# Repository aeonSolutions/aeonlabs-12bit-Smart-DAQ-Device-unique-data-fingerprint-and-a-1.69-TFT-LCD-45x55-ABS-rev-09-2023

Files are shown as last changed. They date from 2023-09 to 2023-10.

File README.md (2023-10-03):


  
 
 

<a href="https://trackgit.com">
trackgit-views
</a>


[PCB-Prototyping-Catalogue](https://github.com/aeonSolutions/PCB-Prototyping-Catalogue)  >>  [Laboratory Automation](https://github.com/aeonSolutions/PCB-Prototyping-Catalogue/tree/main/Laboratory%20Automation)  >>  [Smart DAQ](https://github.com/aeonSolutions/PCB-Prototyping-Catalogue/tree/main/Smart%20DAQ)  >> [12-bit Smart DAQs](https://github.com/aeonSolutions/PCB-Prototyping-Catalogue/tree/main/Smart%20DAQ/12-bit) >> 12-bit Smart DAQ Device with unique data fingerprint and a 1.69" TFT LCD  45x55 ABS

<br>

# 12bit Smart DAQ Device with unique data fingerprint and a 1.69" TFT LCD 45x55 ABS (revision 10-2023)
This is the repository for revision "10-2023" of the 12-bit Smart DAQ Device with a unique data fingerprint able to do experimental data upload to any data repository.

<p align="center">
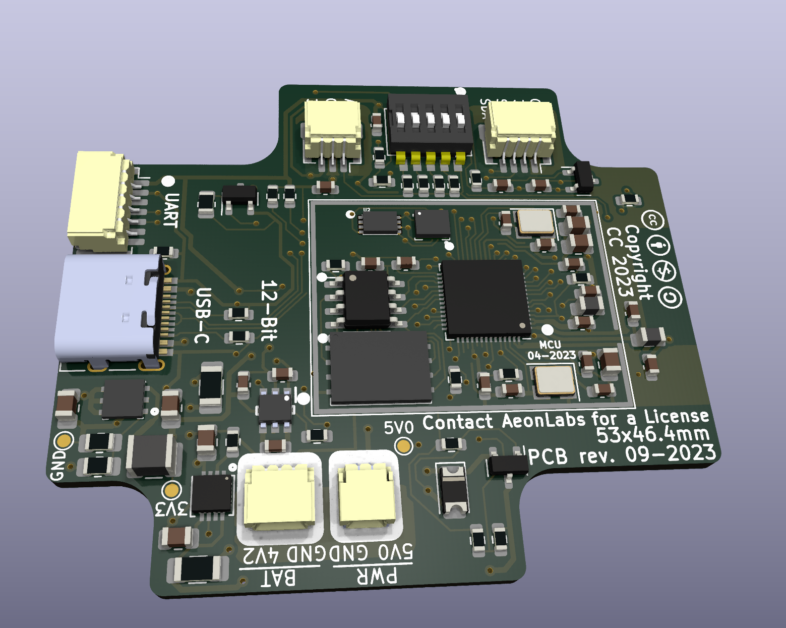
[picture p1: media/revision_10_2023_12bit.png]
   
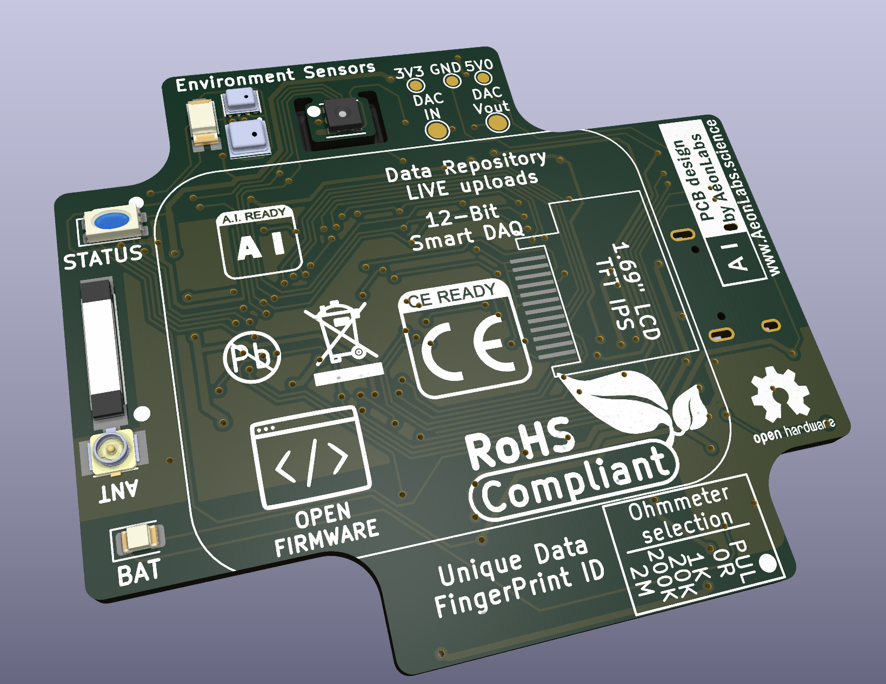
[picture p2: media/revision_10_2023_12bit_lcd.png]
   
</p>

<br>
<br>

**Status**

Fully working

<br>

## Known faults
- PCB copper track optimizations
- components rearrangement for optimization of PCB track inductance 

<br>
<br>

## Dataverse API C library

This device uses my C++ library to expedite dataverse API integration on smart DAQ devices or elsewhere. Follow the link to its repository:

https://github.com/aeonSolutions/OpenScience-Dataverse-API-C-library

<p align="center">
<a href="https://github.com/aeonSolutions/OpenScience-Dataverse-API-C-library"> 
    
 
</a>
 
</p>

<br>
<br>



The photo above is one of the many specimens I purposely fabricated to research self-sensing properties of asphalt mixed with a known content of carbon fibers. This is a 10cm cylinder specimen and on the top is already setup my own design smart #DAQ (get it here on my GitHub ) with the ability to upload LIVE experimental data to a #dataverse.

In the photo above the smart DAQ is installed on an acrylic case and screwed with plastic screws to an acrylic base with the same cross-section area as the specimen to be tested. 
The acrylic base can be bought [here](https://s.click.aliexpress.com/e/_DEGsZaL). And the acrylic case [here](https://s.click.aliexpress.com/e/_Dmudkjt). 

<br>
<br>

### Smart PCB Hardware Specifications
The hardware specifications for the 12bit pcb with dimensions of 23.5x43.5mm are the following:

- QFN 56 Dual Xtensa LX7 Core Processors running up to 240MHz
  -	RISC V ultra-low power co-processor
  - 512Kb RAM (PSRAM max 1 Gb);
  - 16Mb SOIC 8 NOR SPI Flash Memory (max 1Gb);
  - 2.4GHz ISM wireless connectivity;
  - Up to 118 12bit ADC Multiplexed DAQ channels;
- Authentication & Security:
  - SOIC-8 ATSHA204A SHA-256 high-security hardware authentication IC for secure and unique experimental data exchange
- Power management
  - DFN-6 AUR9718 high efficiency step-down 3.3V 1.5A DC converter;
- Onboard sensors:
  - DFN-8 SHT3.x; temperature sensor with a precision of 1.5C;
  - DFN-8 SHT3.x humidity sensor;
  - LGA-14 LSM6DS3 a 6-axis accelerometer and gyroscope;
  - reference voltage sensor calibration with temperature and humidity
- 	External connectivity for up to 118 sensors:
  -  1x I2C pin terminal connector (shared)
  -  1x 12 to 16bit (oversampling & digitization) digital terminal connector (shared)
  -  1x 12 to 16bit (oversampling & digitization) analog terminal connector (shared) with manual scale selection ohmmeter via jumper pin
  -  12 to 16bit (oversampling & digitization) voltage reference analyzer with temperature compensation 
- 1.69 inch TFT IPS LCD  

<br>
<br>

 **In real life this smart DAQ is able to:**
- connect to all kinds of 3V to 5V Digital sensors;
- connect to all kinds of sensors compatible with the I2C protocol. (max 118 sensors simultaneously)
- measure voltage in the range of  [0;3.3V]
- measure electrical resistance [0; 10^6] Ohm 
- do temperature and humidity compensation on all measurements 
- has a voltage reference sensor for improved accuracy on ADC measurements  
- has a motion sensor to know if anyone moved a specimen during an experiment
- ability to show live experimental data on the 1.69-inch TFT IPS LCD  

<br>
<br>

## PCB circuit Schematic 
The PCB circuit schematic is available in PDF located in the folder "PCB Schematic"
<br>

## PCB design files
The PCB gerber files are located in the folder "gerber" and are ready to order online at any PCB fabrication store. (PCBWay, AllPCB, Eurocircuits, etc)
<br>
<br>

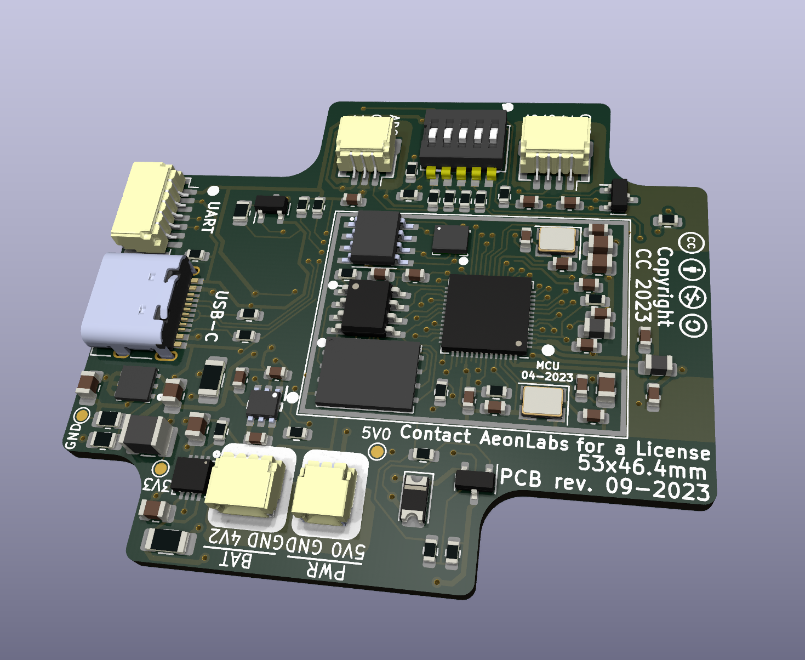
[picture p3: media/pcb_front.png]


<br>
<br>

## Proof of Concept

To test and validate proposed smart DAQ PCB electronics and its firmware as a solution for LIVE experimental data measurements on any test specimen part of a experimental campaign, This PCB electronics is being used to measure a predefined set of variables/parameters to further study several asphalt mixtures with known carbon fiber weight content in the asphalt matrix. Below is a YouTube link to an unedited short video showing one of the experimental setups.

(https://youtu.be/eOA1JPgop0k)

<br />
<br />
<br />

______________________________________________________________________________________________________________________________
### License
2022 Creative Commons Attribution-NonCommercial-ShareAlike 4.0 International

https://creativecommons.org/licenses/by-nc-sa/4.0/

______________________________________________________________________________________________________________________________

<br />
<br />

### Be supportive of my dedication and work towards technology education and buy me a cup of coffee
Buy me a cup of coffee, a slice of pizza or a book to help me study, eat and think new PCB design files.

[](https://www.buymeacoffee.com/migueltomas)

<br />
<br />

### Make a donation on Paypal
Make a donation on paypal and get a TAX refund*.

(http://paypal.me/mtpsilva)

### Support all these open hardware projects and become a patreon  
Liked any of my PCB KiCad Designs? Help and Support my open work to all by becomming a LDAD Patreon.
In return I will give a free PCB design in KiCad to all patreon supporters. To learn more go to patreon.com. Link below.

(https://www.patreon.com/ldad)

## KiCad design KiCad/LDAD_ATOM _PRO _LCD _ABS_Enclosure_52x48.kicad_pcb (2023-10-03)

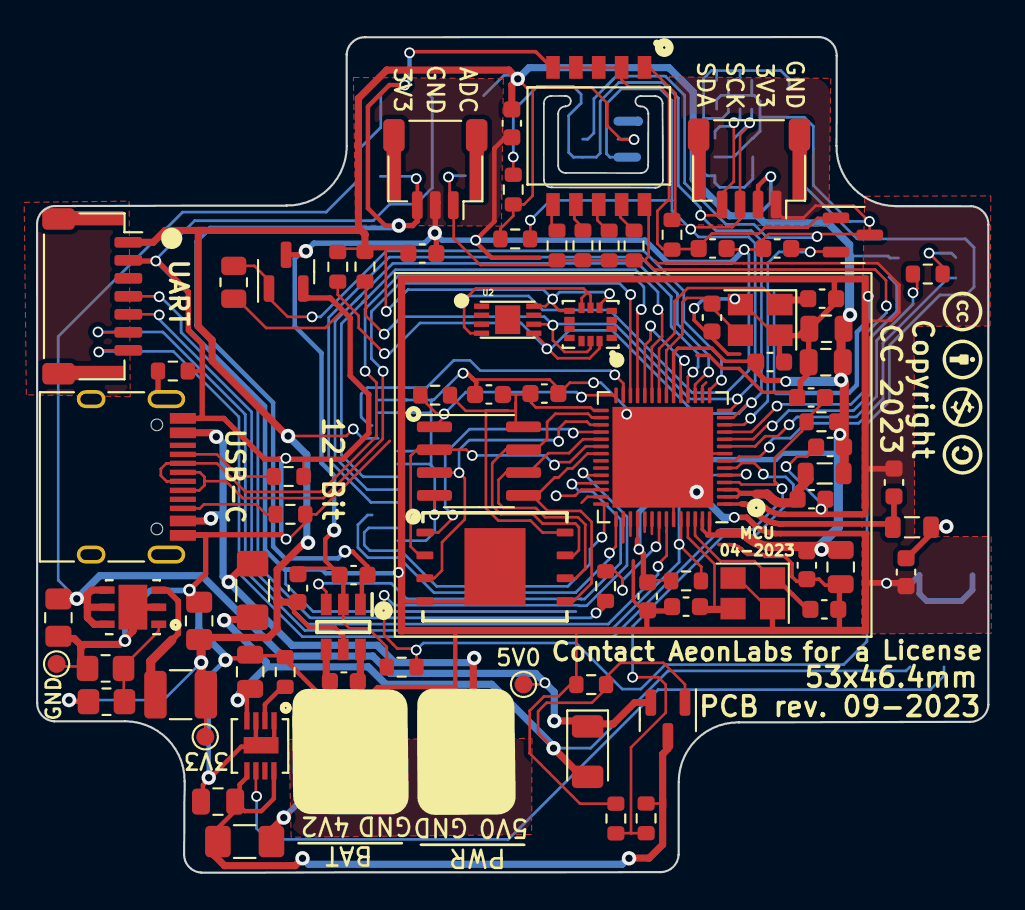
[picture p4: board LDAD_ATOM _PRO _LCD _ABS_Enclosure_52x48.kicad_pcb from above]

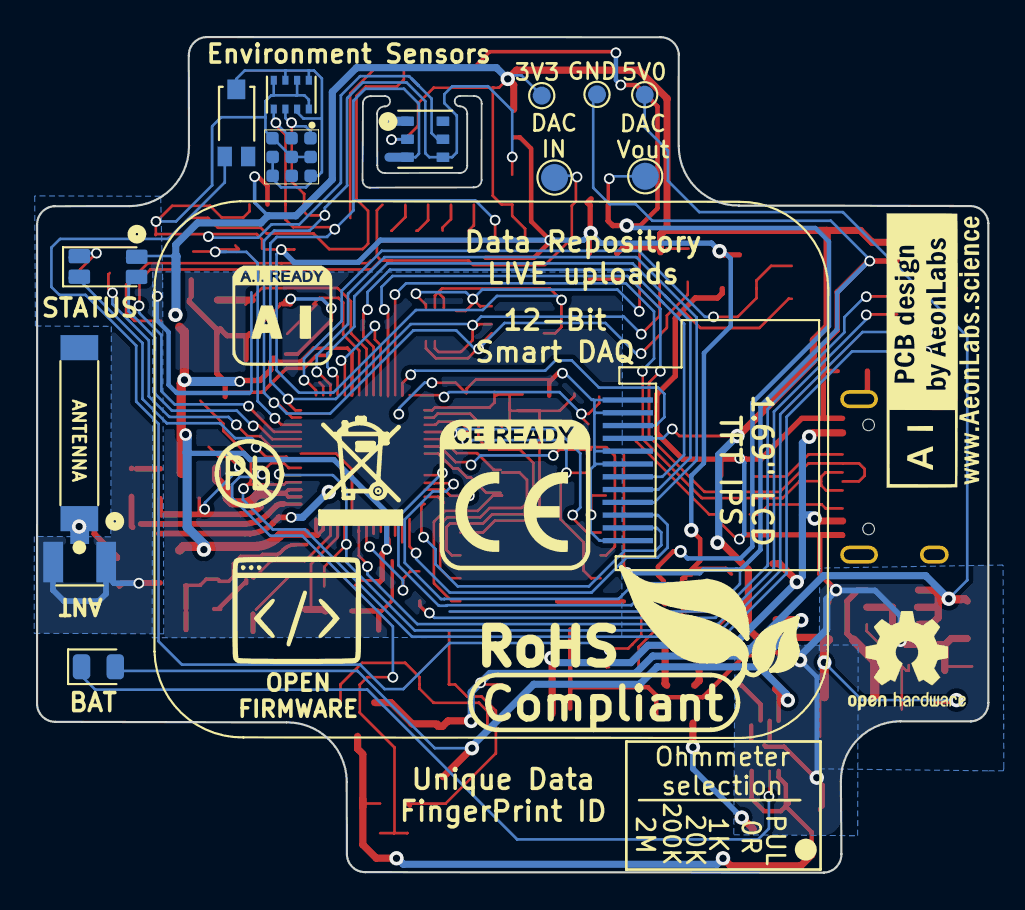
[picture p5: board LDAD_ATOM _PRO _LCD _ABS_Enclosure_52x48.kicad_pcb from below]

Board: 2 copper layers, 52.9 x 46.4 mm, 98 parts (15 on the bottom side), 64 nets.

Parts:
ATH20_C1: 100nF; C_0603_1608Metric
ATSHA_C1: 100nF; C_0603_1608Metric
AUR1: AUR9718x_DFN_3x3mm_6_pin; AUR9718 ST1S09 SON95P300X300X100-7N
AUR_C1: 22uF; C_0805_2012Metric_Pad1.18x1.45mm_HandSolder
AUR_C2: 4.7uF; C_0805_2012Metric_Pad1.18x1.45mm_HandSolder
AUR_R1: 75k; R_0805_2012Metric_Pad1.20x1.40mm_HandSolder
AUR_R2: 24k; R_0805_2012Metric_Pad1.20x1.40mm_HandSolder
AUR_l1: 3.3uF; L_1210_3225Metric
BAT_FUSE1: Polyfuse; Fuse_1206_3216Metric_Pad1.42x1.75mm_HandSolder
BAT_SENSE_R1, BAT_SENSE_R2: 100k; R_0603_1608Metric
CN3065_C2: 4.7uF; C_0805_2012Metric
CN3065_R1: 1K8; R_0603_1608Metric
CN3065_STDBY_LED1: LED; LED_0805_2012Metric
CN3965_C1: 22uF; C_0805_2012Metric
DIPSW1: Conn_02x05_Odd_Even; Dip Switch 5pin 1mm SW_DS05-127-2-06BK-SMT-TR
DIP_R1: 4k7; R_0603_1608Metric
DIP_R2: 1k; R_0603_1608Metric
DIP_R3: 20k; R_0603_1608Metric
DIP_R4: 200k; R_0603_1608Metric
DIP_R5: 2M; R_0603_1608Metric
DMP1045U_1: DMP1045U; SOT-23
DMP1045_R1: 10K; R_0603_1608Metric
DMP1045_SCHOT1: D_Schottky; D_1206_3216Metric
EPS1: ESP32-PSRAM_LY68L6400S; SOIC-8_3.9x4.9mm_P1.27mm
ESP32S1: ESP32-S3; QFN-56-1EP_7x7mm_P0.4mm_EP5.6x5.6mm
ESP32_SHIELD1: RFShield_OnePiece; ESP32-S3 GND Shield
ESP_FLASH1: W25Q128JVS; WSON8 FLASH SPI SON127P800X600X80-9N
E_DTR_R1: 10k; R_0603_1608Metric
E_LNA_ANT1: AN9520; 2.4ghZ WIFI ANTENNA AN9520_ANT2-SMD-9.5X2.1X1.0MM
E_LNA_ANT2: U.FL-R-SMT(01); RF Antenna IPEX SMD PCB HRS_U.FL-R-SMT(01)
E_LNA_C1, E_LNA_C2: 2.7pF; C_0603_1608Metric
E_LNA_l1: 1.8nH 5%; L_0805_2012Metric
E_RTS_C1: 100nF; C_0603_1608Metric
E_RTS_R1: 10k; R_0603_1608Metric
E_SPI_C1: 1uF 10% 50V; C_0603_1608Metric
E_SPI_C2: 100nF 10% 16V; C_0603_1608Metric
E_UART_TX_1: 499R; R_0603_1608Metric
E_VDDA_C1: 100nF; C_0603_1608Metric
E_VDDA_C2: 1uF 10% 50V; C_0805_2012Metric
E_VDD_3_C1, E_VDD_3_C2: 10uF 20% 6.3V; C_0805_2012Metric
E_VDD_3_C3, E_VDD_3_C4: 100nF 10% 16V; C_0603_1608Metric
E_VDD_CPU_C1: 100nF 10% 16V; C_0603_1608Metric
E_VDD_L1: 12nH 5%; L_0805_2012Metric
E_VDD_RTC_C1: 100nF 10% 16V; C_0603_1608Metric
E_XTAL32_1: 32.768Mhz 22pF+-10PPM; Crystal_SMD_3225-4Pin_3.2x2.5mm
E_XTAL32_C1, E_XTAL32_C2, E_XTAL40_C1, E_XTAL40_C2: 22pF 5% 50V; C_0603_1608Metric
E_XTAL40_1: 40Mhz 22pF+-10PPM; Crystal_SMD_3225-4Pin_3.2x2.5mm
ExtSW1: Conn_01x03_Female; JST_SH_SM03B-SRSS-TB_1x03-1MP_P1.00mm_Horizontal
ExtSWBAT_PLUG2: Conn_01x03_Female; JST_SH_SM03B-SRSS-TB_1x03-1MP_P1.00mm_Horizontal
HX1: HX4002; HX4002 SOT95 P280X125-6N
HX_C1, HX_C2, HX_C3: 2.2uF; C_0603_1608Metric
I2C_PLUG1: I2C6; JST_SH_SM04B-SRSS-TB_1x04-1MP_P1.00mm_Horizontal
I2C_SCL_R1, I2C_SDA_R1: 10k; R_0603_1608Metric
IC_ENS1: ENS160 Gas Semsor
IMR1, IMR2: 10K; R_0603_1608Metric
IMU1: LSM6DS3; LSM6DS3 Motion Sensor PQFN50P300X250X86-14N
J1: TYPE-C-31-M-12; USB_C_Receptacle_HRO_TYPE-C-31-M-12
JICSP1: Conn_01x07_Socket; JST_SH_SM07B-SRSS-TB_1x07-1MP_P1.00mm_Horizontal
LCD1: Conn_01x12_Male; 1,69 inch LCD IPS TFT
LED1: LED_GBRC; LED_1206_3210_RGB_Metric
LR1: 330R; R_0603_1608Metric
MTRR1: 10k; R_0805_2012Metric
MTRT1: NPN; SOT-23
PSRAM_R1: 100K; R_0603_1608Metric
PWR_FUSE1: Polyfuse; Fuse_1206_3216Metric_Pad1.42x1.75mm_HandSolder
PWR_PLUG1: Screw_Terminal_01x02; JST_SH_SM02B-SRSS-TB_1x02-1MP_P1.00mm_Horizontal
Sign-PbFree: LOGO_PBFREE
Sign-RecycleBin: LOGO_RECYCLEBIN_1
Sign-RoHS: LOGO_ROHS_1
TMPR1: 10K; R_0603_1608Metric
TP1, TP1#2: VIN; TestPoint_Pad_D1.0mm
TP2, TP2#2: VOut; TestPoint_Pad_D1.0mm
TP3, TP3#2: GND; TestPoint_Pad_D1.0mm
U1: MCP1525-TT; SOT-23
U2: ATSHA204A-MAHDA-T; ATSHA204 UDFN-8 DFN200X300X60-9N
U3: Battery_charger_CN3065_QFN8; QFN8 3.1x2.9mm QFNn-8 3x3 SON80P400X400X100-9N
U4: AHT20; AHT20 HT Sensor PSON100P300X300X110-6N
U5: BMP280; XDCR_BMP280
U6: TEMT6000; TEMT6000-SEN
USB_PLUG_R1, USB_PLUG_R3: 5k1; R_0603_1608Metric
USB_PLYG_R2: 150K; R_0603_1608Metric
VOLTAGE_REF_C1, VOLTAGE_REF_C2: 100nF; C_0603_1608Metric

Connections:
3V3: ATH20_C1.2, ATSHA_C1.2, AUR_C1.1, AUR_R1.1, AUR_l1.1, ESP32S1.20 (VDD3P3_RTC), ESP32S1.46 (VDD3P3_CPU), ESP32S1.55 (VDDA), ESP32S1.56 (VDDA), E_DTR_R1.1, E_RTS_R1.1, E_VDDA_C1.2, E_VDDA_C2.2, E_VDD_3_C1.1, E_VDD_3_C2.1, E_VDD_3_C3.1, E_VDD_CPU_C1.1, E_VDD_L1.1, E_VDD_RTC_C1.1, HX1.5 (VIN), HX_C3.2, I2C_PLUG1.2, I2C_SCL_R1.1, I2C_SDA_R1.2, IC_ENS1.4 (VDD), IC_ENS1.5 (VDDIO), IC_ENS1.7 (CS), IMR1.1, IMR2.1, IMU1.5 (VDDIO), IMU1.8 (VDD), JICSP1.1, LCD1.4, LED1.4 (K), TP2.1, TP2#2.1, U2.8 (VCC), U4.2 (VDD), U5.2 (CSB), U5.6 (VDDIO), U5.8 (VDD), U6.COLLECTOR
3V3_PLUG: DIPSW1.3, DIPSW1.5, DIPSW1.7, DIPSW1.9, DIP_R1.2, ExtSW1.3, HX1.1 (VOUT), HX_C1.1, U1.1 (Vin), VOLTAGE_REF_C1.2
ADC_IN_IO04: DIPSW1.2, DIP_R2.1, DIP_R3.1, DIP_R4.1, DIP_R5.1, ESP32S1.11 (GPIO6/ADC1_CH5), ExtSW1.1
BAT_SENSE_IO21: BAT_SENSE_R1.1, BAT_SENSE_R2.2, ESP32S1.6 (GPIO1/ADC1_CH0)
CHIP_EN: ESP32S1.4 (CHIP_PU/RESET), E_RTS_C1.2, E_RTS_R1.2, JICSP1.7
DAC_CALIBRATION: ESP32S1.19 (GPIO14/ADC2_CH3), ESP32S1.24 (GPIO18/ADC2_CH7/DAC_1)
ESP_GPIO0_BOOT-DTR: ESP32S1.5 (GPIO0/BOOT), ESP32S1.52 (GPIO46), E_DTR_R1.2, JICSP1.6
GND: AUR1.2 (GND), AUR1.7 (GND), AUR_C1.2, AUR_C2.2, AUR_R2.2, BAT_SENSE_R1.2, CN3065_C2.1, CN3065_R1.1, CN3965_C1.1, DMP1045_R1.2, EPS1.4 (VSS), ESP32S1.8 (GPIO3/ADC1_CH2), ESP32S1.51 (GPIO45), ESP32S1.57 (GND), ESP32_SHIELD1.1 (Shield), ESP_FLASH1.4 (GND), ESP_FLASH1.9 (GND), E_LNA_ANT2.1 (GND), E_LNA_ANT2.2 (GND), E_LNA_C1.2, E_LNA_C2.2, E_RTS_C1.1, E_SPI_C1.2, E_SPI_C2.2, E_VDDA_C1.1, E_VDDA_C2.1, E_VDD_3_C1.2, E_VDD_3_C2.2, E_VDD_3_C3.2, E_VDD_3_C4.2, E_VDD_CPU_C1.2, E_VDD_RTC_C1.2, E_XTAL32_1.2, E_XTAL32_1.4, E_XTAL32_C1.2, E_XTAL32_C2.2, E_XTAL40_1.2, E_XTAL40_1.4, E_XTAL40_C1.2, E_XTAL40_C2.2, ExtSWBAT_PLUG2.3, J1.B1, J1.B12, JICSP1.2, LCD1.1, LCD1.2, LCD1.5, LCD1.6, LCD1.12, MTRR1.1, MTRT1.2, PWR_PLUG1.1, TP3.1, TP3#2.1, U3.1 (V_Temp), U3.3 (GND), U3.9 (GND), USB_PLUG_R1.2, USB_PLUG_R3.2, USB_PLYG_R2.2
GNDD: ATH20_C1.1, ATSHA_C1.1, ExtSW1.2, HX1.2 (GND), HX_C1.2, HX_C3.1, I2C_PLUG1.1, IC_ENS1.3 (MISO), IC_ENS1.8 (VSS), IC_ENS1.9 (VSS), IMU1.6 (GND), IMU1.7 (GND), MTRT1.3, TMPR1.1, U1.3 (Vss), U2.4 (GND), U4.5 (GND), U5.1 (GND), U5.5 (SDO), U5.7 (GND), VOLTAGE_REF_C1.1, VOLTAGE_REF_C2.1
GPIO8_I2C_SDA: ESP32S1.13 (GPIO8/ADC1_CH7), I2C_PLUG1.4, I2C_SDA_R1.1, IC_ENS1.1 (SDA), IMR1.2, IMU1.14 (SDA), U2.5 (SDA), U4.4 (SDA), U5.3 (SDI)
GPIO9_I2C_SCL: ESP32S1.14 (GPIO9/ADC1_CH8), I2C_PLUG1.3, I2C_SCL_R1.2, IC_ENS1.2 (SCL), IMR2.2, IMU1.13 (SCL), U2.6 (SCL), U4.3 (SCL), U5.4 (SCK)
LCD_CS_IO13: ESP32S1.18 (GPIO13/ADC2_CH2), LCD1.8
LCD_DC_IO17: ESP32S1.23 (GPIO17/ADC2_CH6/DAC_2), LCD1.7
LCD_I2C_SCL_IO12: ESP32S1.17 (GPIO12/ADC2_CH1), LCD1.9
LCD_I2C_SDA_IO38: ESP32S1.43 (GPIO38), LCD1.10
LCD_LED_IO21: ESP32S1.27 (GPIO21), LCD1.3
LCD_RST_IO37: ESP32S1.42 (GPIO37), LCD1.11
LED_B_IO05: ESP32S1.10 (GPIO5/ADC1_CH4), LED1.2 (BA)
LED_G_IO02: ESP32S1.7 (GPIO2/ADC1_CH1), LED1.1 (GA)
LED_R_IO04: ESP32S1.9 (GPIO4/ADC1_CH3), LR1.1
unnamed: AUR1.1 (FB), AUR_R1.2, AUR_R2.1
unnamed: AUR1.3 (SW), AUR_l1.2
unnamed: DIPSW1.1, DIP_R1.1
unnamed: DIPSW1.4, DIP_R2.2
unnamed: DIPSW1.6, DIP_R3.2
unnamed: DIPSW1.8, DIP_R4.2
unnamed: DIPSW1.10, DIP_R5.2
unnamed: ESP32S1.21 (GPIO15/ADC2_CH4/XTAL_32K_P), E_XTAL32_1.3, E_XTAL32_C1.1
unnamed: ESP32S1.22 (GPIO16/ADC2_CH5/XTAL_32K_N), E_XTAL32_1.1, E_XTAL32_C2.1
unnamed: ESP32S1.1 (LNA_IN/RF), E_LNA_C2.1, E_LNA_l1.2
unnamed: ESP32S1.49 (U0TXD/PROG/GPIO43), E_UART_TX_1.2
unnamed: ESP32S1.2 (VDD3P3), ESP32S1.3 (VDD3P3), E_VDD_3_C4.1, E_VDD_L1.2
unnamed: ESP32S1.53 (XTAL_N), E_XTAL40_1.3, E_XTAL40_C2.1
unnamed: ESP32S1.54 (XTAL_P), E_XTAL40_1.1, E_XTAL40_C1.1
unnamed: E_LNA_ANT1.1, E_LNA_ANT2.3 (SIG), E_LNA_C1.1, E_LNA_l1.1
unnamed: HX1.6 (C+), HX_C2.1
unnamed: HX1.4 (C-), HX_C2.2
unnamed: J1.A5 (CC1), USB_PLUG_R3.1
unnamed: J1.B5 (CC2), USB_PLUG_R1.1
unnamed: J1.S1 (SHIELD), USB_PLYG_R2.1
unnamed: LED1.3 (RA), LR1.2
unnamed: CN3065_R1.2, U3.2 (I_SET)
PERIPHERALS_PWR_EN_IO10: ESP32S1.15 (GPIO10/ADC1_CH9), MTRR1.2, MTRT1.1
PLUG_PWR_3V3_EN_IO38: ESP32S1.39 (GPIO34), HX1.3 (EN)
RXD0: ESP32S1.50 (U0RXD/PROG/GPIO44), JICSP1.5
SPICLK: EPS1.6 (SCLK), ESP32S1.33 (SPICLK/GPIO30), ESP_FLASH1.6 (CLK)
SPICS0: ESP32S1.32 (SPICS0/GPIO29), ESP_FLASH1.1 (~CS)
SPICS1: EPS1.1 (~CE), ESP32S1.28 (SPI_CS1/GPIO26), PSRAM_R1.1
SPID: EPS1.5 (SiO0), ESP32S1.35 (SPID/GPIO32), ESP_FLASH1.5 (DI(IO0))
SPIHD: EPS1.7 (SIO3), ESP32S1.30 (SPIHD/GPIO27), ESP_FLASH1.7 (IO3)
SPIQ: EPS1.2 (SIO1), ESP32S1.34 (SPIQ/GPIO31), ESP_FLASH1.2 (DO(IO1))
SPIWP: EPS1.3 (SIO2), ESP32S1.31 (SPIWP/GPIO28), ESP_FLASH1.3 (IO2)
STDBY_LED_G: CN3065_STDBY_LED1.1 (K), U3.6 (LED_DONE)
TEMT6000_IO33: ESP32S1.38 (GPIO33), TMPR1.2, U6.EMITTER
TXD0: E_UART_TX_1.1, JICSP1.4
USB_5V0: CN3065_STDBY_LED1.2 (A), CN3965_C1.2, DMP1045U_1.1, DMP1045_R1.1, DMP1045_SCHOT1.2 (A), PWR_FUSE1.1, U3.4 (VIN)
USB_5V0F: J1.A4, J1.A9, PWR_FUSE1.2, PWR_PLUG1.2
USB_D+: ESP32S1.26 (GPIO20/USB_D+/ADC2_CH9), J1.A6 (DP1), J1.B6 (DP2)
USB_D-: ESP32S1.25 (GPIO19/USB_D-/ADC2_CH8), J1.A7 (DN1), J1.B7 (DN2)
VDD_SPI: EPS1.8 (VCC), ESP32S1.29 (VDD_SPI), ESP_FLASH1.8 (VCC), E_SPI_C1.1, E_SPI_C2.1, PSRAM_R1.2
VIN: AUR1.4 (VIN_SW), AUR1.5 (VIN_A), AUR1.6 (EN), AUR_C2.1, DMP1045U_1.2, DMP1045_SCHOT1.1 (K), TP1.1, TP1#2.1
VIN_BAT: BAT_FUSE1.1, BAT_SENSE_R2.1, CN3065_C2.2, DMP1045U_1.3, U3.5 (BAT+), U3.8 (FB)
VIN_BATF: BAT_FUSE1.2, ExtSWBAT_PLUG2.1
VOLTAGE_REF_IO07: ESP32S1.12 (GPIO7/ADC1_CH6), U1.2 (Vout), VOLTAGE_REF_C2.2
